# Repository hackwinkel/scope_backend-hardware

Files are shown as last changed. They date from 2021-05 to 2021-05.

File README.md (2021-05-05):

# 100Ms/s dual channel 16 bitdigital oscilloscope and function generator back-end with ethernet 

This repository contains the schematics and PCB design files.

# Main features
- 100MHz sample rate
- 2 channels, 16 bits A/D
- 4 channels, 14 bits D/A
- 256 Mbyte ddr3 ram
- Gigabit Ethernet

# General description
Please refer to the hierarchical schematic diagram provided in this repository

* Main (contains various digital power supplies and references to subsheets)
   * FPGA (contains the FPGA with its power connections, JTAG and signal definitions)
   * DACS (contains the D / A convertors with analogue power supplies and output buffers)
   * ADCS (contains the A/D convertors with analogue power supplies and input buffers)
   * ddr3 (contains memory with terminations)
   * GNET (contains Gbit ethernet PHY with magnetics and support components)

## Power supplies
All power supplies are standard LDO regulators, stepping down the voltages from a main 5V connection. To limit dissipation in each LDO, multiple 3.3V, 2.5V, 1.5V and 1.2V subnets are used, and the lower voltages are stepped down via an intermediary 3.3V stage.
The only exception is an optional switched mode power supply module providing +9V/-9V for analogue input/output buffers. This module is optional if the analogue front-end is used, as this also provides these voltages.

## FPGA
This project uses a SPARTAN 6 Field Programmable Logic Array (XC6SLX16 FPLA) at its heart. This FPLA device digitally connects all components, and allows this project to be flexibly reconfigured for various purposes. Core timing is provided by a 100MHz integrated crystal oscillator and a 125MHz clock derived from the ethernet PHY 

## DACS
Digital-to-Analogue conversion is performed by 4 DAC904 165 Msample/s 14 bit D/A convertors. Each of these D/A convertors has its own 3.3V power supply. The DAC904 produces a differential output signal, which is converted and buffered to a single ended signal using an OPA695 operational amplifier.

## ADCS
Analogue-to-Digital conversion is performed by 2 LTC2208 130 Msample/s 16 bit A/D convertors. Each of these A/D convertors has its own 3.3V power supply. For each A/D convertor an AD8138 diferential amplifier provides the required buffered differential analogue drive signal. These AD8138 are by default configured to convert a single ended signal to a differential signal.

## ddr3
A single MT41K128M16 ddr3 RAM chip provides 128M x 16 memory. This has to be a 1.5V compatible device as the SPARTAN 6 FPGA does not support 1.35V memory. Single ended, single direction lines (address and some control signals) are unterminated as this apparently "just works"-albeit probably not at maximum speed. Bidirectional signals are dynamically terminated on the chip. Simple resistive termination is provided on some differential clocking signals. A reference voltage is generated using a resistive divider. All traces on the PCB are length-matched to within 0.5mm

## GNET
A KSZ9031 Gigabit ethernet PHY with Reduced Gigabit Media Independent Interface (RGMII) provides a gigabit ethernet connection through a gigabit MagJack. The local 25Mhz crystal oscillator is converted to a 125MHz clock signal, which is also connected to the FPGA as an alternate timing source

## This project is currently under construction
Most notably, VHDL/Verilog code to program the FPGA is required and an analogue front-end.

# IMPORTANT NOTE FOR PCB FABRICATION

Various PCB houses have various design constraints. JLCPCB has some awkward design rules, requiring a larger space between via-pads and adjacent traces of different nets than between two traces of different nets. KiCAD only allows you to specify *one* spacing for both. In order to accomodate this, the PCB has been designed using 0.508mm vias with 0.2mm holes. Prior to exporting to gerbers, these via pads need to be made smaller in order to compy with these design rules:

Pcbnew -> Setup -> Design rules, change "Via Dia" to 0.45mm
Pcbnew -> Edit -> Edit All Tracks and Vias -> Set all vias (no tracks) to their Netclass value, and OK

## EXPORT GERBERS, DO NOT SAVE THE CHANGED PCB DESIGN FILES as next time you change anything the smaller vias will lead to planes and traces coming too close to the via.

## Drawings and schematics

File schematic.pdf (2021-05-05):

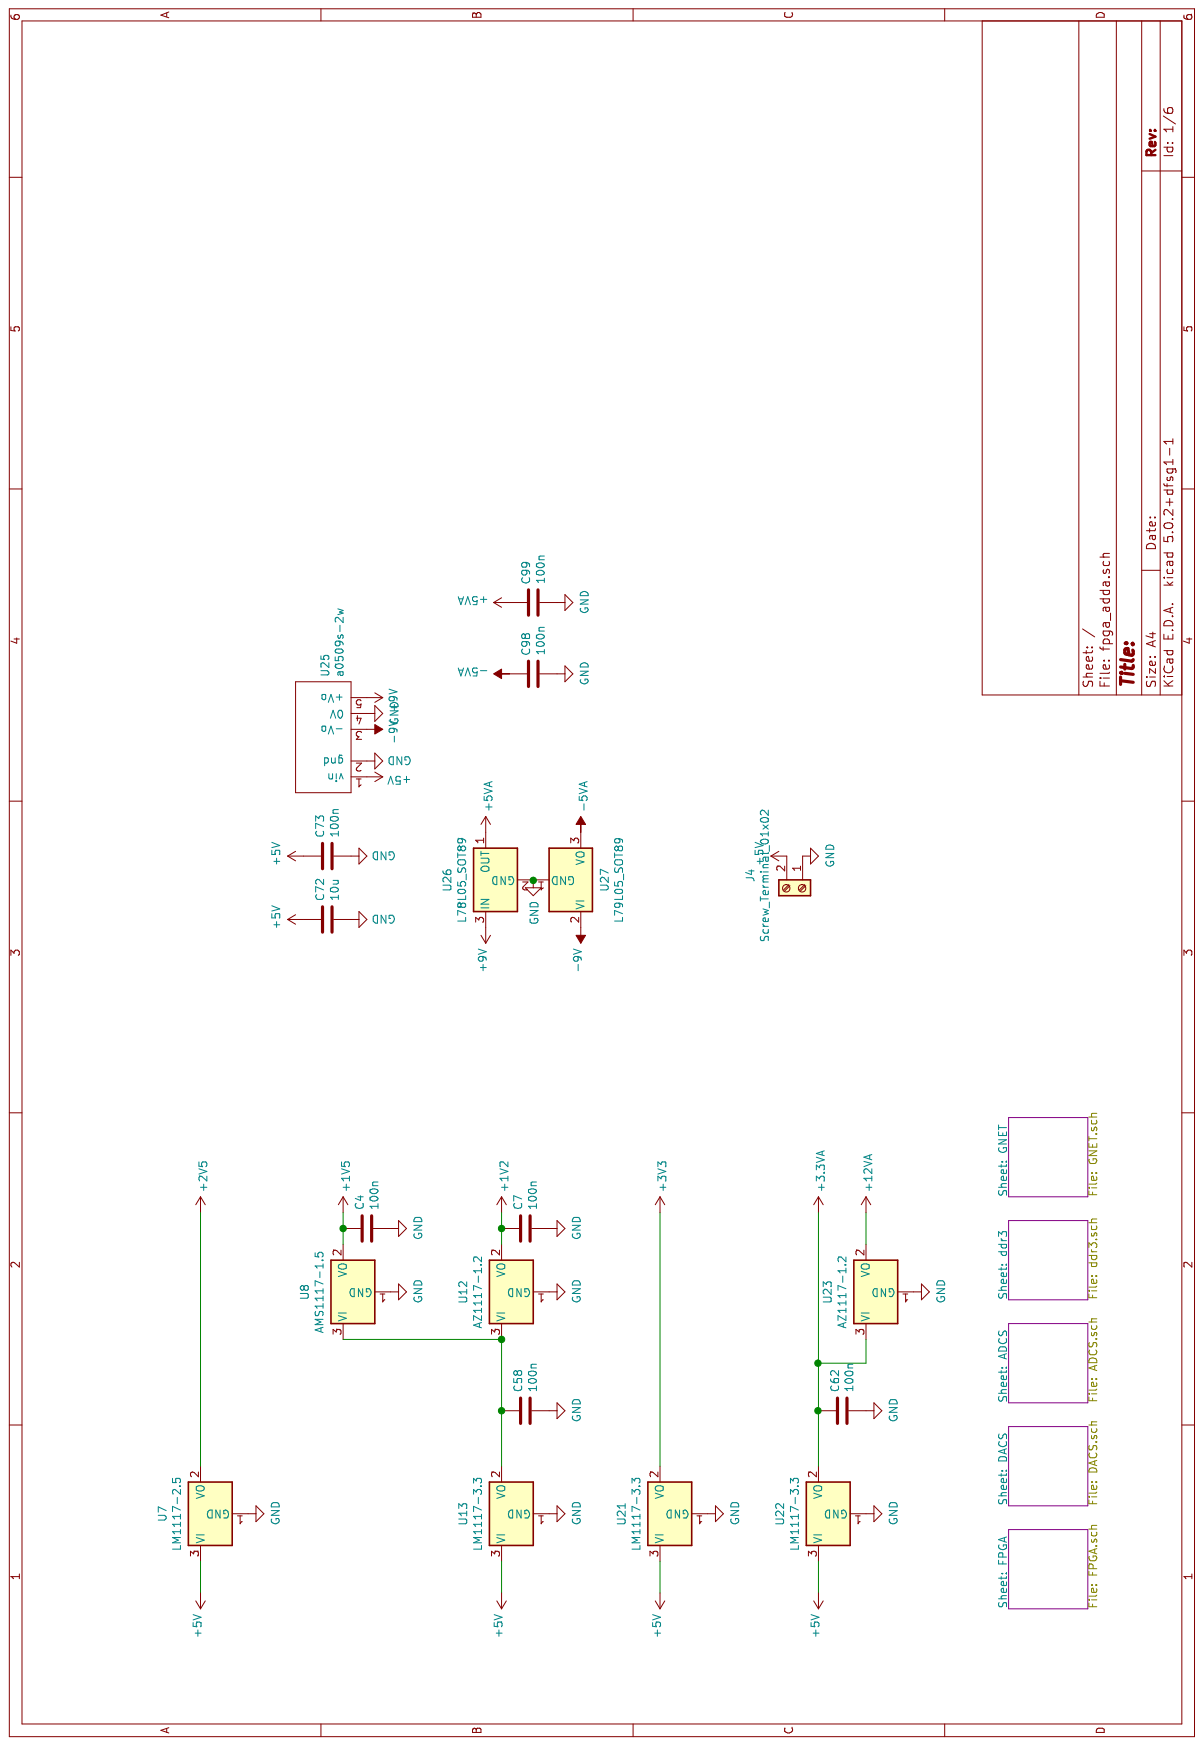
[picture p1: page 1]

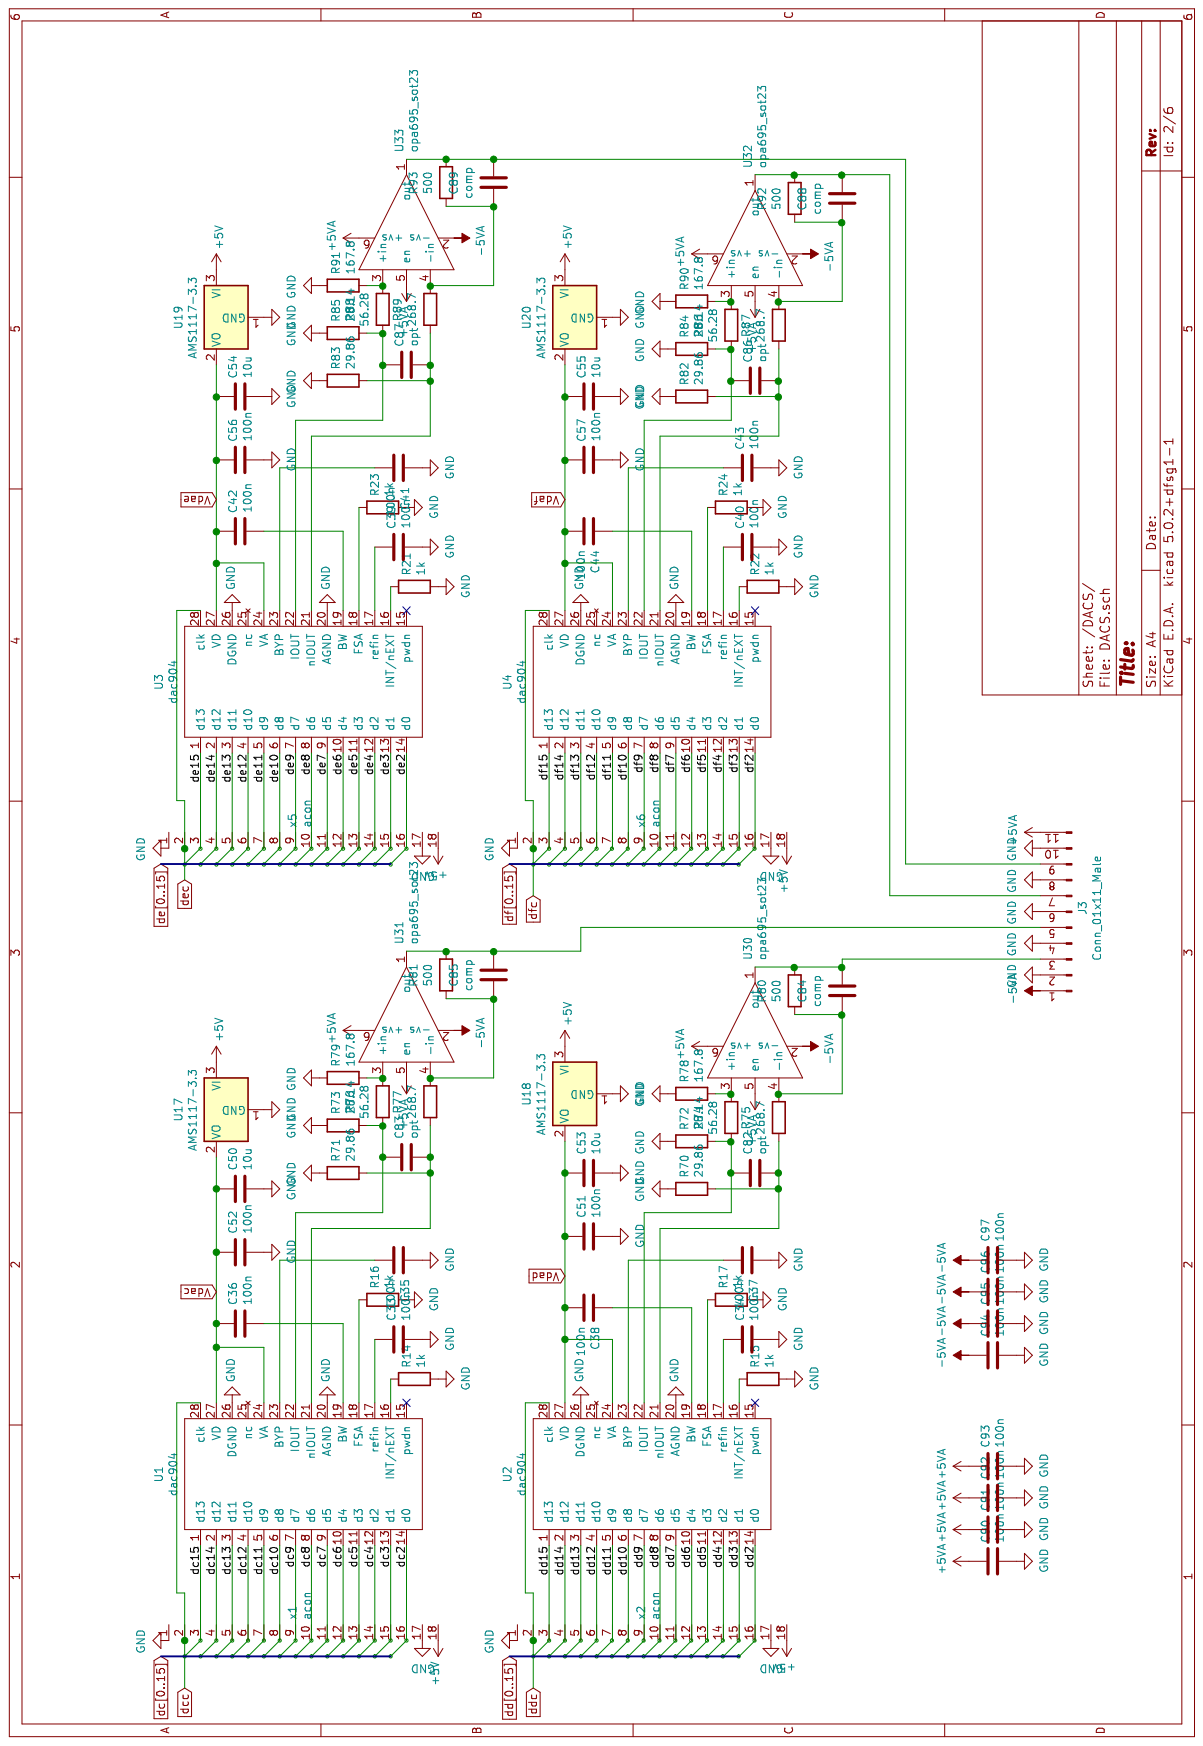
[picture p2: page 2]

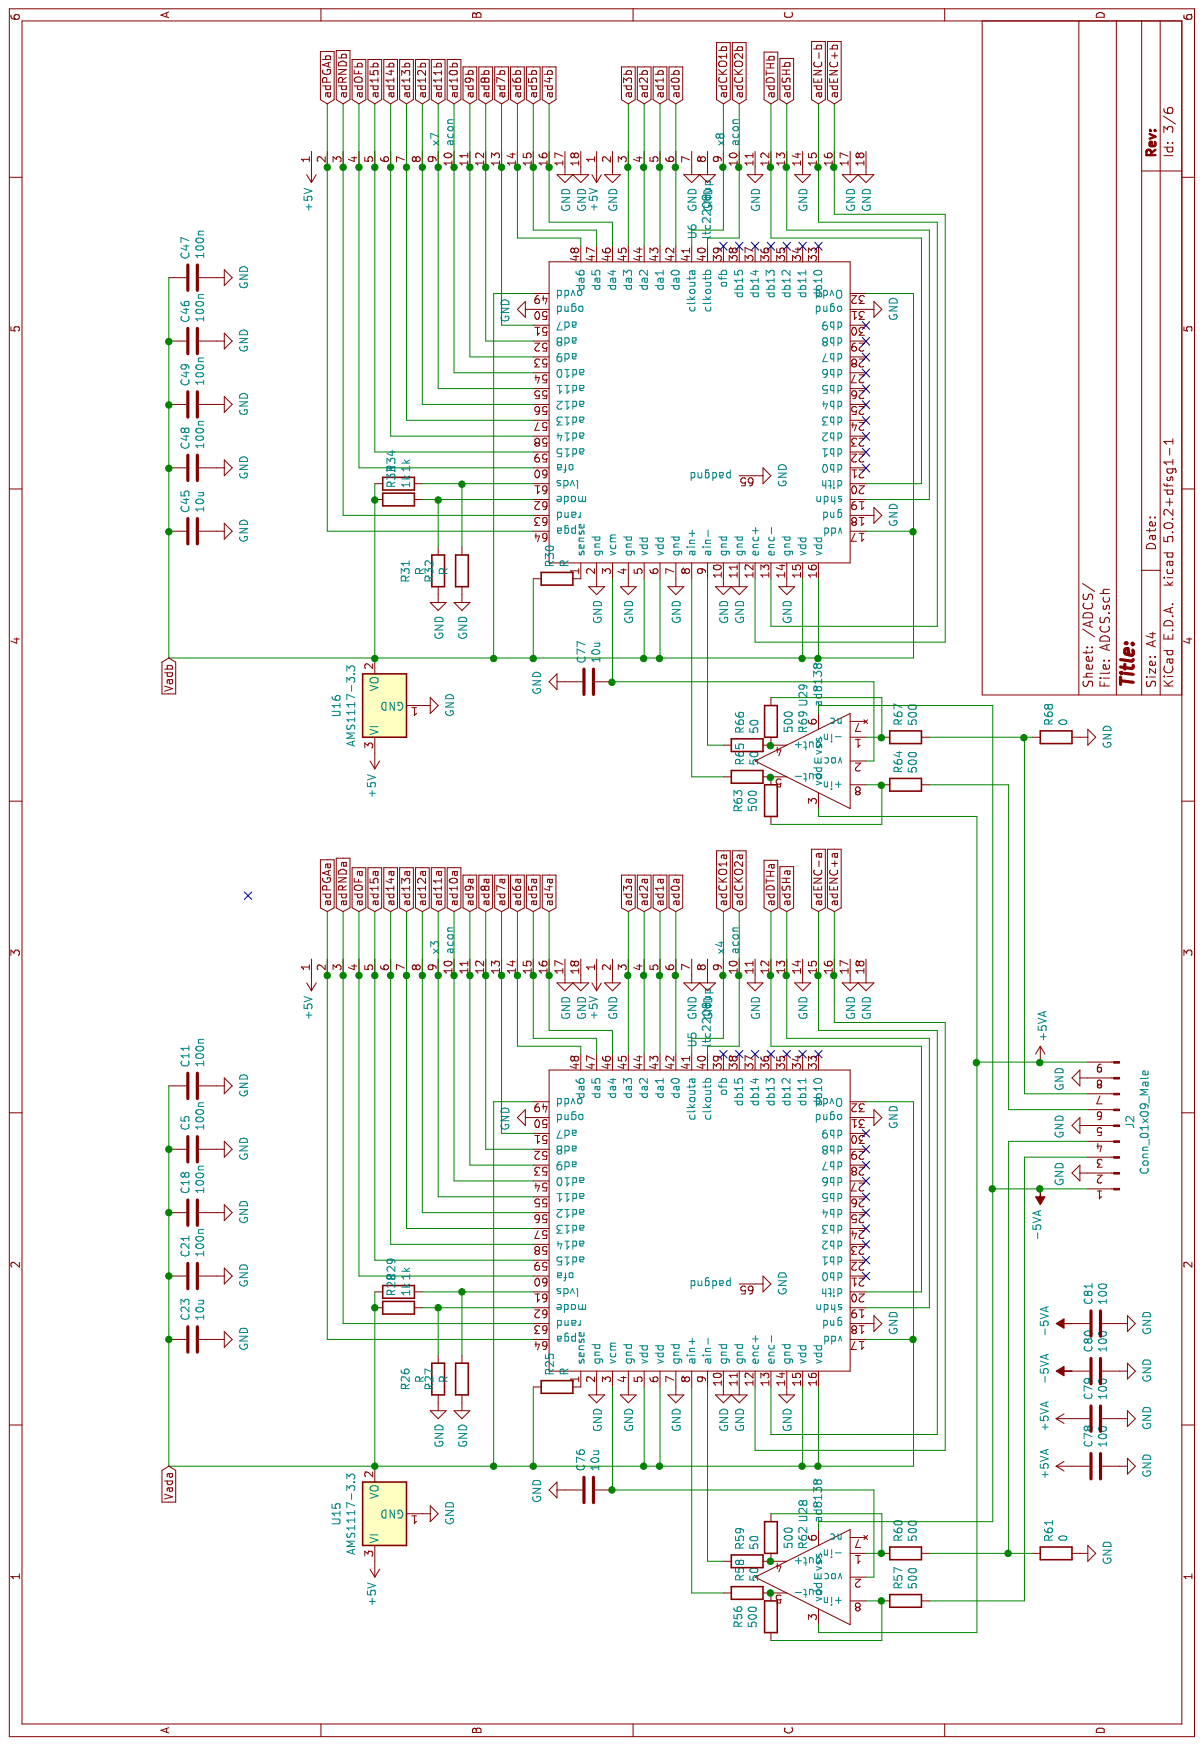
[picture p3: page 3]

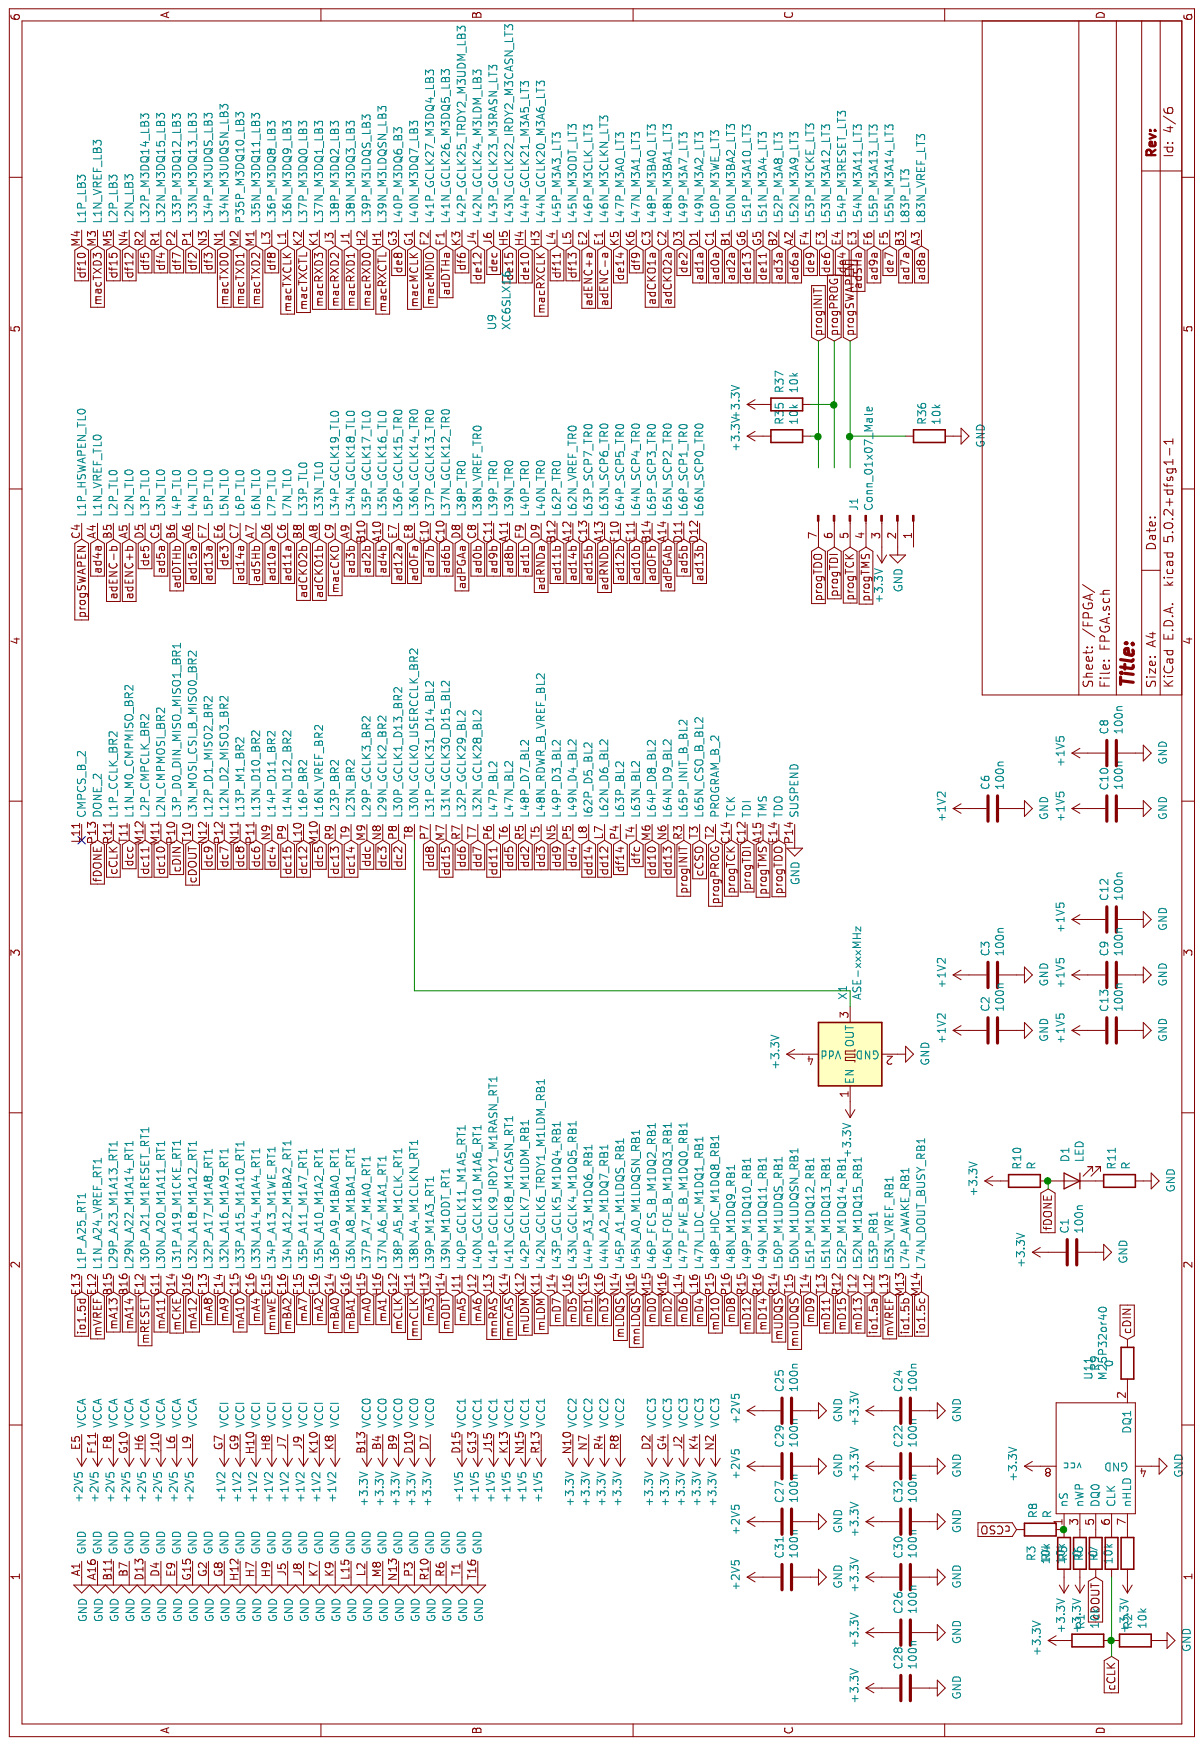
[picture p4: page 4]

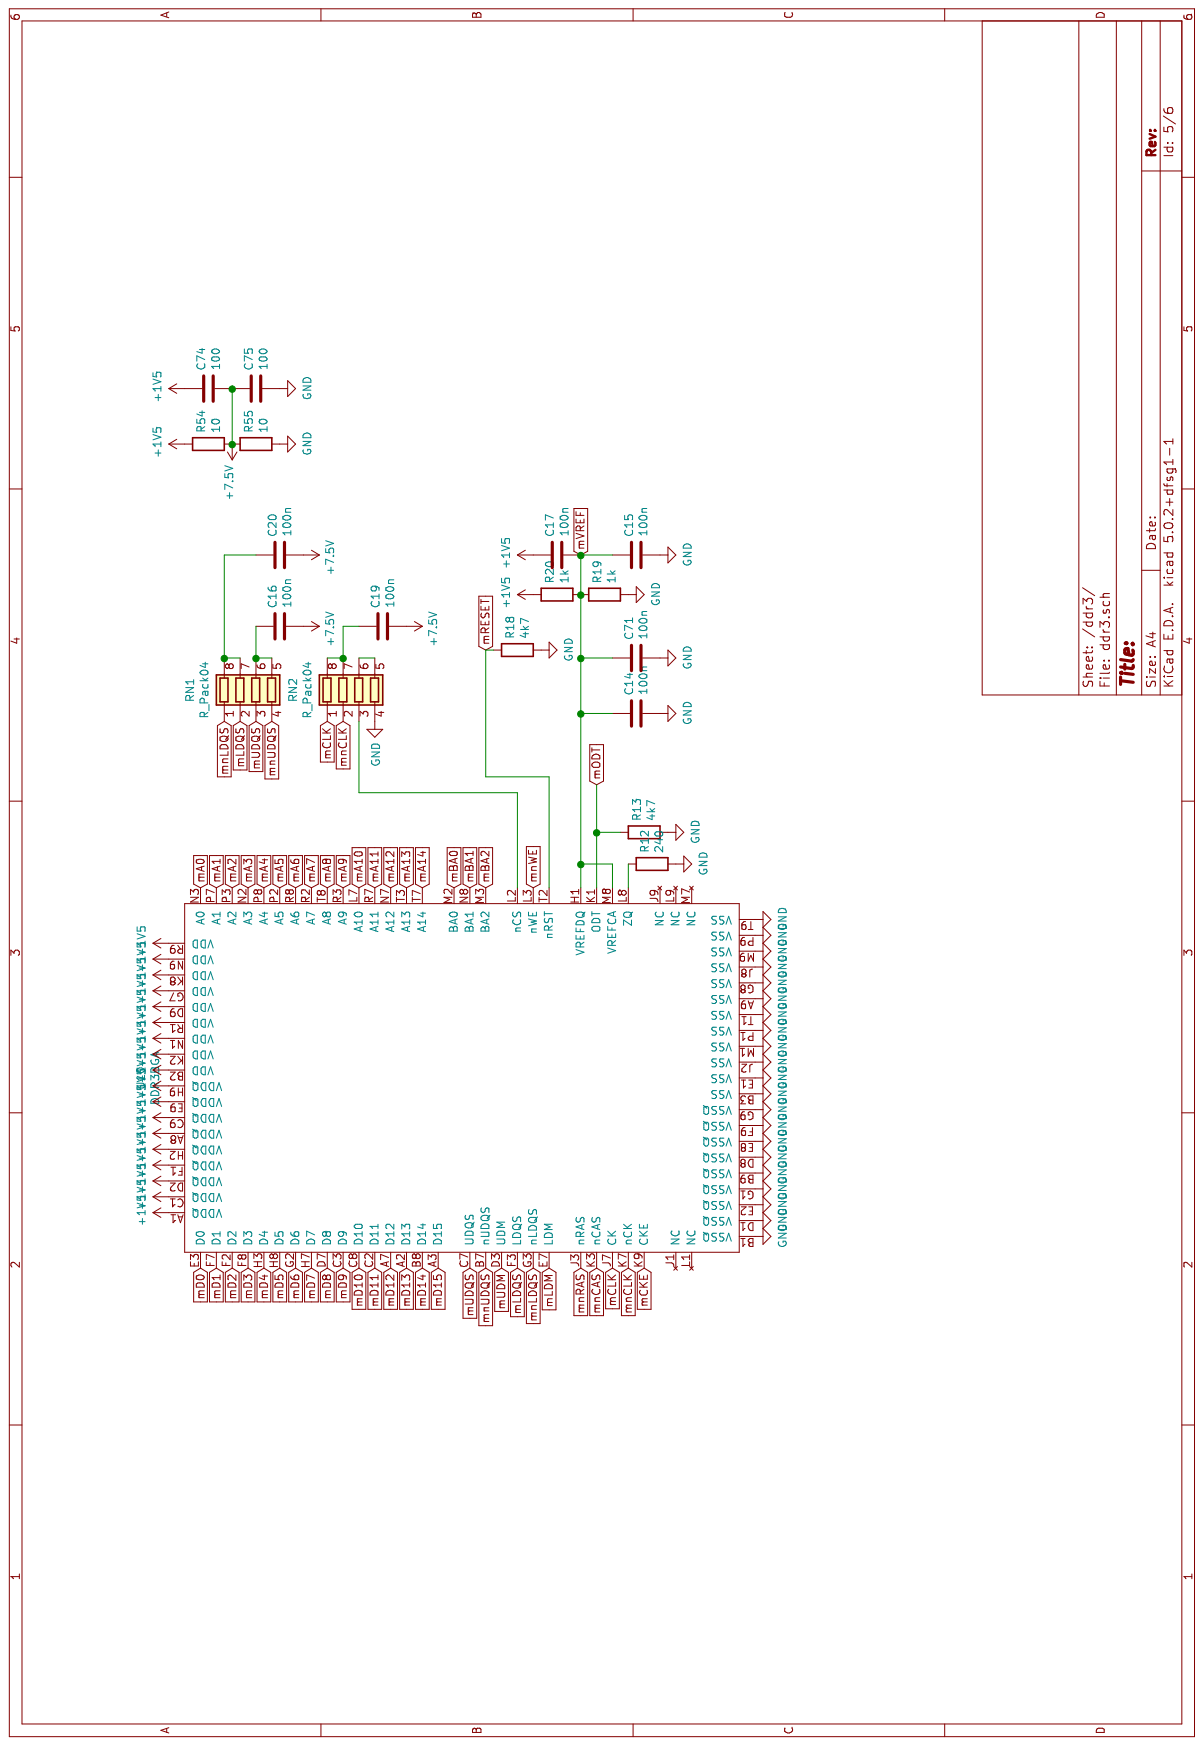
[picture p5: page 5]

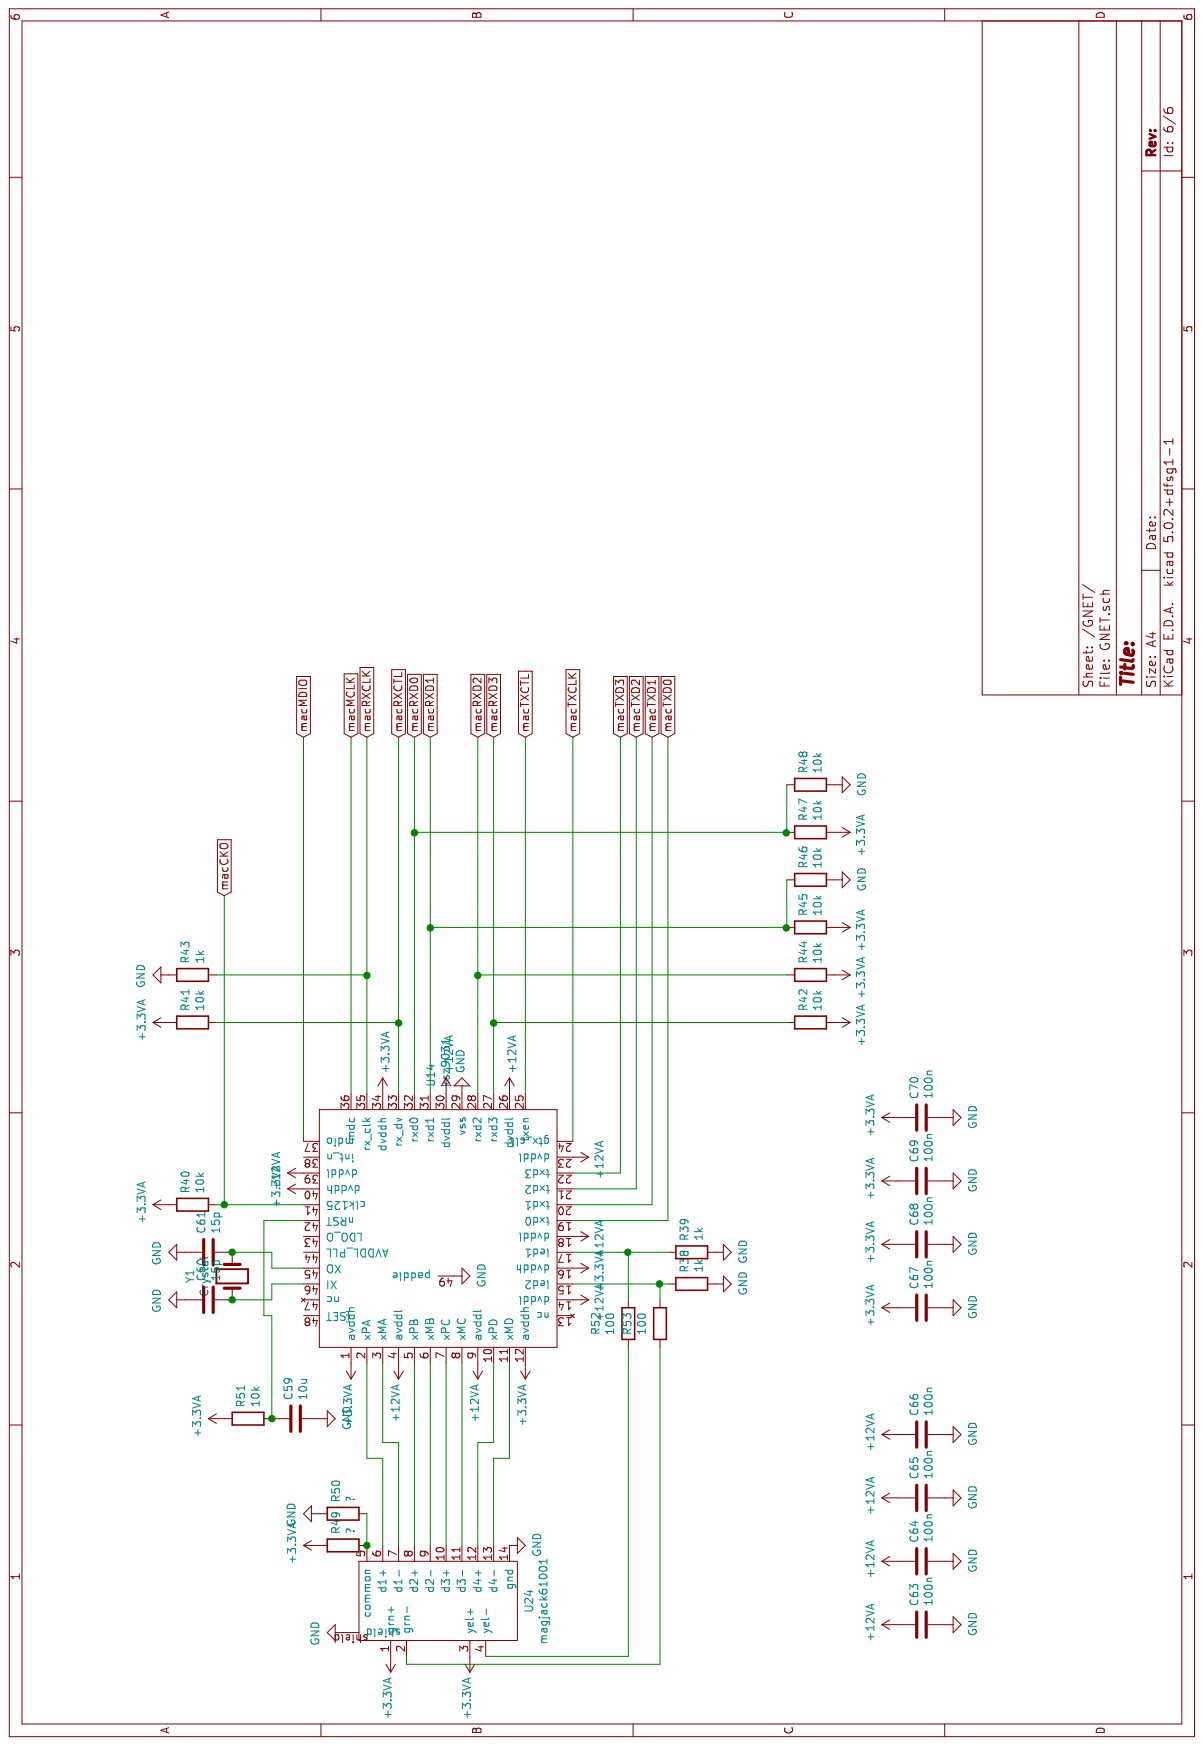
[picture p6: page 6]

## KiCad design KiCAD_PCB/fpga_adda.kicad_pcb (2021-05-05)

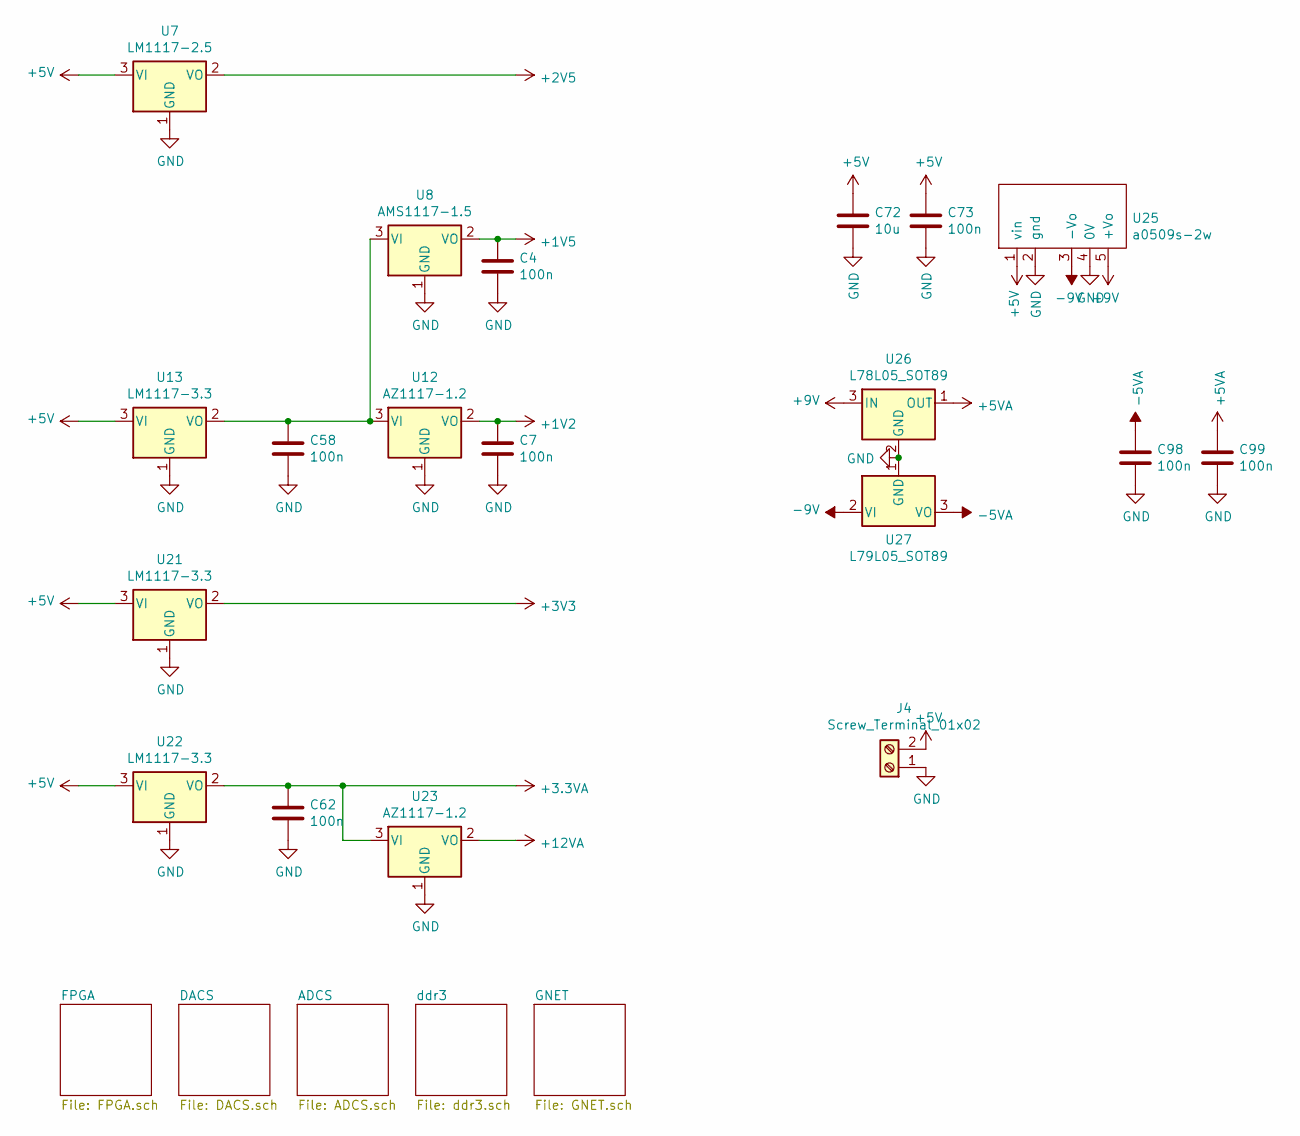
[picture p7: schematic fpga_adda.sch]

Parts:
C4, C7, C58, C62, C73, C98, C99: 100n; C_0805_2012Metric_Pad1.15x1.40mm_HandSolder
C72: 10u; C_0805_2012Metric_Pad1.15x1.40mm_HandSolder
J4: Screw_Terminal_01x02; TerminalBlock_bornier-2_P5.08mm
U7: LM1117-2.5; SOT-223-3_TabPin2
U8: AMS1117-1.5; SOT-223-3_TabPin2
U12, U23: AZ1117-1.2; SOT-223-3_TabPin2
U13, U21, U22: LM1117-3.3; SOT-223-3_TabPin2
U25: a0509s-2w
U26: L78L05_SOT89; SOT-89-3
U27: L79L05_SOT89; SOT-89-3

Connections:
+1V2: C7.1, U12.2 (VO); also elsewhere on the board
+1V5: C4.1, U8.2 (VO); also elsewhere on the board
+2V5: U7.2 (VO); also elsewhere on the board
+3.3VA: C62.1, U22.2 (VO), U23.3 (VI); also elsewhere on the board
+5V: C72.1, C73.1, J4.2, U7.3 (VI), U13.3 (VI), U21.3 (VI), U22.3 (VI), U25.1 (vin); also elsewhere on the board
+5VA: C99.1, U26.1 (OUT); also elsewhere on the board
+9V: U25.5 (+Vo), U26.3 (IN)
+12VA: U23.2 (VO); also elsewhere on the board
-5VA: C98.1, U27.3 (VO); also elsewhere on the board
-9V: U25.3 (-Vo), U27.2 (VI)
GND: C4.2, C7.2, C58.2, C62.2, C72.2, C73.2, C98.2, C99.2, J4.1, U7.1 (GND), U8.1 (GND), U12.1 (GND), U13.1 (GND), U21.1 (GND), U22.1 (GND), U23.1 (GND), U25.2 (gnd), U25.4 (0V), U26.2 (GND), U27.1 (GND); also elsewhere on the board
unnamed: C58.1, U8.3 (VI), U12.3 (VI), U13.2 (VO)

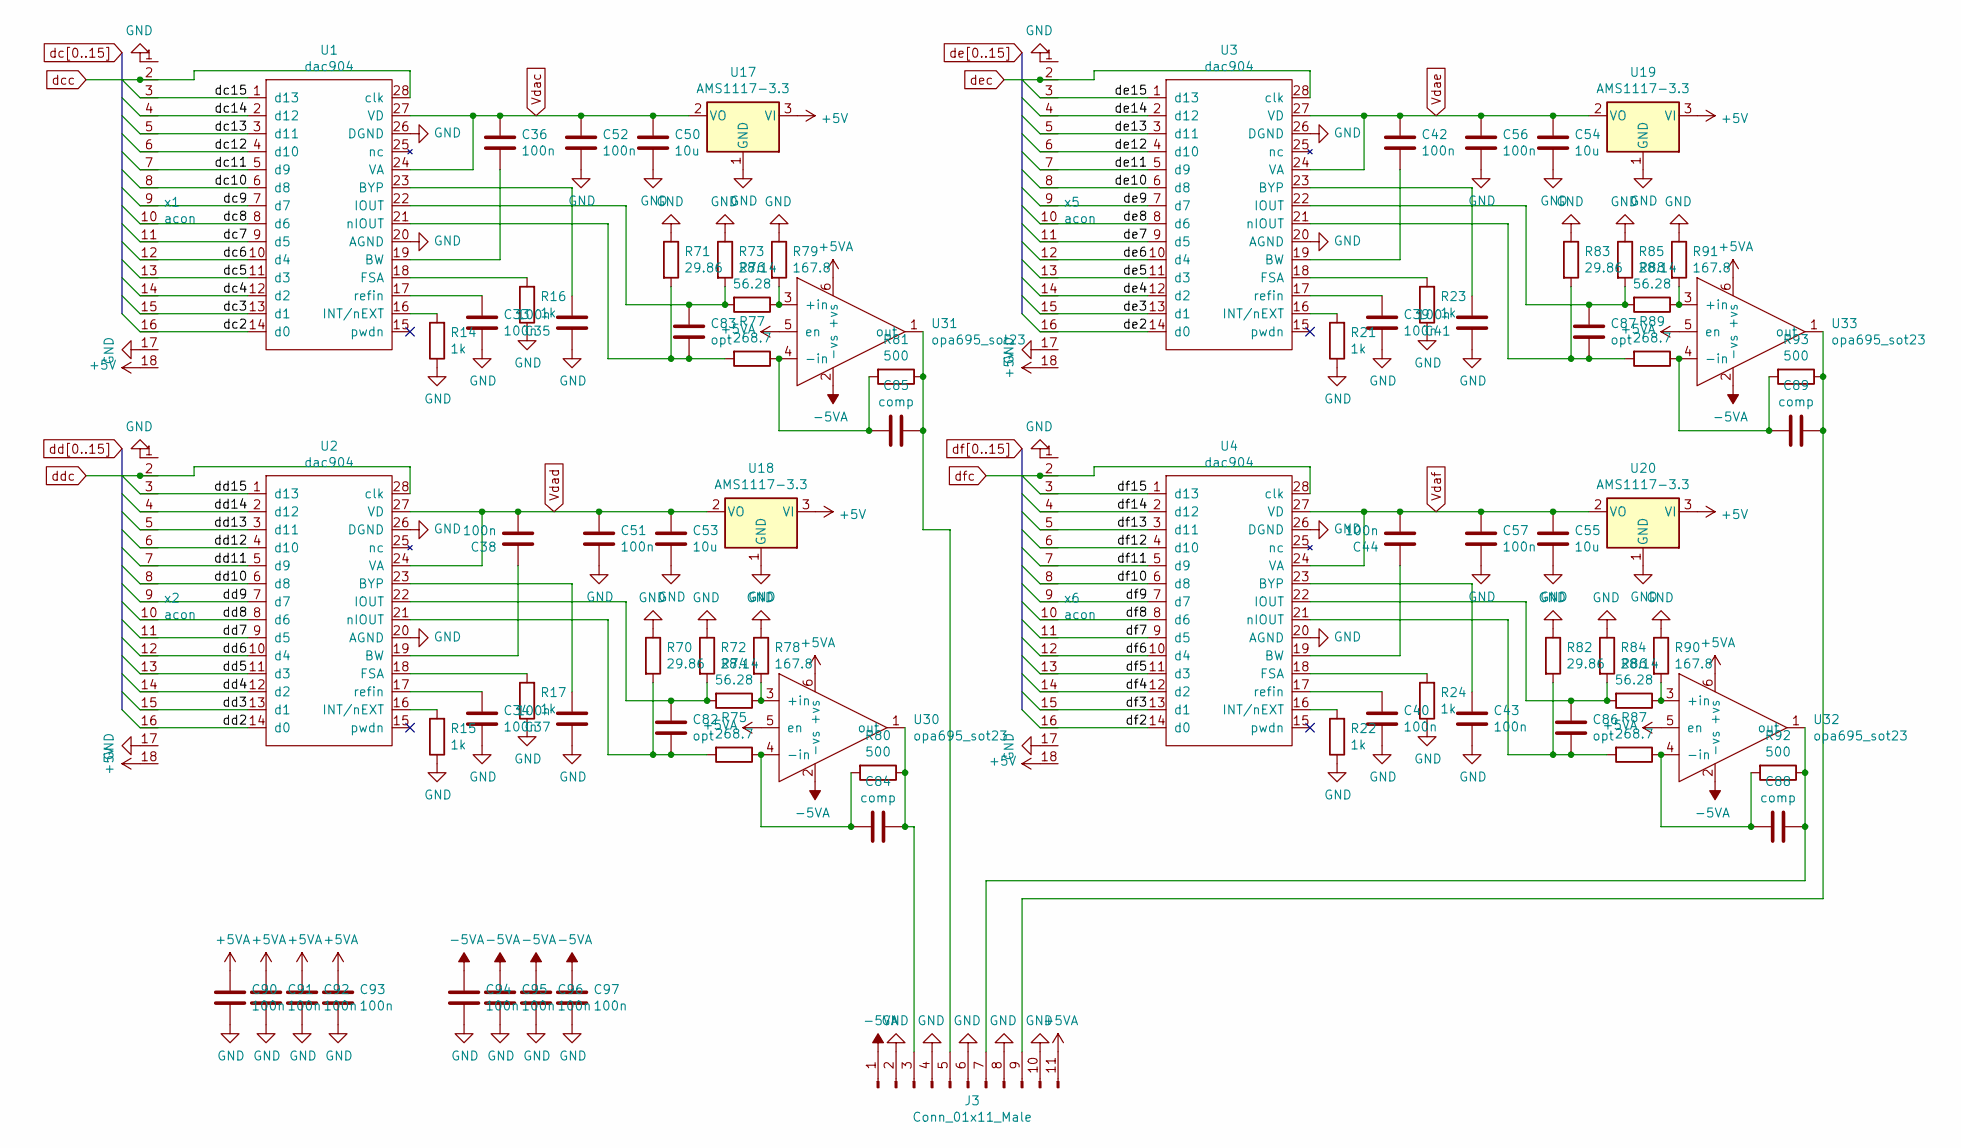
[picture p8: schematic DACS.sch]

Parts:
C33, C34, C35, C36, C37, C38, C39, C40, C41, C42, C43, C44, C51, C52, C56, C57, C90, C91, C92, C93, C94, C95, C96, C97: 100n; C_0805_2012Metric_Pad1.15x1.40mm_HandSolder
C50, C53, C54, C55: 10u; C_0805_2012Metric_Pad1.15x1.40mm_HandSolder
C82, C83, C86, C87: opt; C_0805_2012Metric_Pad1.15x1.40mm_HandSolder
C84, C85, C88, C89: comp; C_0805_2012Metric_Pad1.15x1.40mm_HandSolder
J3: Conn_01x11_Male; PinHeader_1x11_P2.54mm_Vertical
R14, R15, R16, R17, R21, R22, R23, R24: 1k; R_0805_2012Metric_Pad1.15x1.40mm_HandSolder
R70, R71, R82, R83: 29.86; R_0805_2012Metric_Pad1.15x1.40mm_HandSolder
R72, R73, R84, R85: 28.14; R_0805_2012Metric_Pad1.15x1.40mm_HandSolder
R74, R76, R86, R88: 56.28; R_0805_2012Metric_Pad1.15x1.40mm_HandSolder
R75, R77, R87, R89: 268.7; R_0805_2012Metric_Pad1.15x1.40mm_HandSolder
R78, R79, R90, R91: 167.8; R_0805_2012Metric_Pad1.15x1.40mm_HandSolder
R80, R81, R92, R93: 500; R_0805_2012Metric_Pad1.15x1.40mm_HandSolder
U1, U2, U3, U4: dac904; SSOP-28_5.3x10.2mm_P0.65mm
U17, U18, U19, U20: AMS1117-3.3; SOT-223-3_TabPin2
U30, U31, U32, U33: opa695_sot23; SOT-23-6_Handsoldering
x1, x2, x5, x6: acon

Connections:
+5V: U17.3 (VI), U18.3 (VI), U19.3 (VI), U20.3 (VI), x1.18, x2.18, x5.18, x6.18; also elsewhere on the board
+5VA: C90.1, C91.1, C92.1, C93.1, J3.11, U30.5 (en), U30.6 (+vs), U31.5 (en), U31.6 (+vs), U32.5 (en), U32.6 (+vs), U33.5 (en), U33.6 (+vs); also elsewhere on the board
-5VA: C94.1, C95.1, C96.1, C97.1, J3.1, U30.2 (-vs), U31.2 (-vs), U32.2 (-vs), U33.2 (-vs); also elsewhere on the board
GND: C33.2, C34.2, C35.1, C37.1, C39.2, C40.2, C41.1, C43.2, C50.2, C51.2, C52.2, C53.2, C54.2, C55.2, C56.2, C57.2, C90.2, C91.2, C92.2, C93.2, C94.2, C95.2, C96.2, C97.2, J3.2, J3.4, J3.6, J3.8, J3.10, R14.1, R15.1, R16.1, R17.1, R21.1, R22.1, R23.1, R24.1, R70.1, R71.1, R72.1, R73.1, R78.1, R79.1, R82.1, R83.1, R84.1, R85.1, R90.1, R91.1, U1.20 (AGND), U1.26 (DGND), U2.20 (AGND), U2.26 (DGND), U3.20 (AGND), U3.26 (DGND), U4.20 (AGND), U4.26 (DGND), U17.1 (GND), U18.1 (GND), U19.1 (GND), U20.1 (GND), x1.1, x1.17, x2.1, x2.17, x5.1, x5.17, x6.1, x6.17; also elsewhere on the board
unnamed: C33.1, U1.17 (refin)
unnamed: C34.1, U2.17 (refin)
unnamed: C35.2, U1.23 (BYP)
unnamed: C36.2, U1.19 (BW)
unnamed: C37.2, U2.23 (BYP)
unnamed: C38.1, U2.19 (BW)
unnamed: C39.1, U3.17 (refin)
unnamed: C40.1, U4.17 (refin)
unnamed: C41.2, U3.23 (BYP)
unnamed: C42.2, U3.19 (BW)
unnamed: C43.1, U4.23 (BYP)
unnamed: C44.1, U4.19 (BW)
unnamed: C82.1, R72.2, R74.2, U2.22 (IOUT)
unnamed: C82.2, R70.2, R75.2, U2.21 (nIOUT)
unnamed: C83.1, R73.2, R76.2, U1.22 (IOUT)
unnamed: C83.2, R71.2, R77.2, U1.21 (nIOUT)
unnamed: C84.1, J3.3, R80.1, U30.1 (out)
unnamed: C84.2, R75.1, R80.2, U30.4 (-in)
unnamed: C85.1, J3.5, R81.1, U31.1 (out)
unnamed: C85.2, R77.1, R81.2, U31.4 (-in)
unnamed: C86.1, R84.2, R86.2, U4.22 (IOUT)
unnamed: C86.2, R82.2, R87.2, U4.21 (nIOUT)
unnamed: C87.1, R85.2, R88.2, U3.22 (IOUT)
unnamed: C87.2, R83.2, R89.2, U3.21 (nIOUT)
unnamed: C88.1, J3.7, R92.1, U32.1 (out)
unnamed: C88.2, R87.1, R92.2, U32.4 (-in)
unnamed: C89.1, J3.9, R93.1, U33.1 (out)
unnamed: C89.2, R89.1, R93.2, U33.4 (-in)
unnamed: R14.2, U1.16 (INT/nEXT)
unnamed: R15.2, U2.16 (INT/nEXT)
unnamed: R16.2, U1.18 (FSA)
unnamed: R17.2, U2.18 (FSA)
unnamed: R21.2, U3.16 (INT/nEXT)
unnamed: R22.2, U4.16 (INT/nEXT)
unnamed: R23.2, U3.18 (FSA)
unnamed: R24.2, U4.18 (FSA)
unnamed: R74.1, R78.2, U30.3 (+in)
unnamed: R76.1, R79.2, U31.3 (+in)
unnamed: R86.1, R90.2, U32.3 (+in)
unnamed: R88.1, R91.2, U33.3 (+in)
Vdac: C36.1, C50.1, C52.1, U1.24 (VA), U1.27 (VD), U17.2 (VO)
Vdad: C38.2, C51.1, C53.1, U2.24 (VA), U2.27 (VD), U18.2 (VO)
Vdae: C42.1, C54.1, C56.1, U3.24 (VA), U3.27 (VD), U19.2 (VO)
Vdaf: C44.2, C55.1, C57.1, U4.24 (VA), U4.27 (VD), U20.2 (VO)
dc2: U1.14 (d0), x1.16; also elsewhere on the board
dc3: U1.13 (d1), x1.15; also elsewhere on the board
dc4: U1.12 (d2), x1.14; also elsewhere on the board
dc5: U1.11 (d3), x1.13; also elsewhere on the board
dc6: U1.10 (d4), x1.12; also elsewhere on the board
dc7: U1.9 (d5), x1.11; also elsewhere on the board
dc8: U1.8 (d6), x1.10; also elsewhere on the board
dc9: U1.7 (d7), x1.9; also elsewhere on the board
dc10: U1.6 (d8), x1.8; also elsewhere on the board
dc11: U1.5 (d9), x1.7; also elsewhere on the board
dc12: U1.4 (d10), x1.6; also elsewhere on the board
dc13: U1.3 (d11), x1.5; also elsewhere on the board
dc14: U1.2 (d12), x1.4; also elsewhere on the board
dc15: U1.1 (d13), x1.3; also elsewhere on the board
dcc: U1.28 (clk), x1.2; also elsewhere on the board
dd2: U2.14 (d0), x2.16; also elsewhere on the board
dd3: U2.13 (d1), x2.15; also elsewhere on the board
dd4: U2.12 (d2), x2.14; also elsewhere on the board
dd5: U2.11 (d3), x2.13; also elsewhere on the board
dd6: U2.10 (d4), x2.12; also elsewhere on the board
dd7: U2.9 (d5), x2.11; also elsewhere on the board
dd8: U2.8 (d6), x2.10; also elsewhere on the board
dd9: U2.7 (d7), x2.9; also elsewhere on the board
dd10: U2.6 (d8), x2.8; also elsewhere on the board
dd11: U2.5 (d9), x2.7; also elsewhere on the board
dd12: U2.4 (d10), x2.6; also elsewhere on the board
dd13: U2.3 (d11), x2.5; also elsewhere on the board
dd14: U2.2 (d12), x2.4; also elsewhere on the board
dd15: U2.1 (d13), x2.3; also elsewhere on the board
ddc: U2.28 (clk), x2.2; also elsewhere on the board
de2: U3.14 (d0), x5.16; also elsewhere on the board
de3: U3.13 (d1), x5.15; also elsewhere on the board
de4: U3.12 (d2), x5.14; also elsewhere on the board
de5: U3.11 (d3), x5.13; also elsewhere on the board
de6: U3.10 (d4), x5.12; also elsewhere on the board
de7: U3.9 (d5), x5.11; also elsewhere on the board
de8: U3.8 (d6), x5.10; also elsewhere on the board
de9: U3.7 (d7), x5.9; also elsewhere on the board
de10: U3.6 (d8), x5.8; also elsewhere on the board
de11: U3.5 (d9), x5.7; also elsewhere on the board
de12: U3.4 (d10), x5.6; also elsewhere on the board
de13: U3.3 (d11), x5.5; also elsewhere on the board
de14: U3.2 (d12), x5.4; also elsewhere on the board
de15: U3.1 (d13), x5.3; also elsewhere on the board
dec: U3.28 (clk), x5.2; also elsewhere on the board
df2: U4.14 (d0), x6.16; also elsewhere on the board
df3: U4.13 (d1), x6.15; also elsewhere on the board
df4: U4.12 (d2), x6.14; also elsewhere on the board
df5: U4.11 (d3), x6.13; also elsewhere on the board
df6: U4.10 (d4), x6.12; also elsewhere on the board
df7: U4.9 (d5), x6.11; also elsewhere on the board
df8: U4.8 (d6), x6.10; also elsewhere on the board
df9: U4.7 (d7), x6.9; also elsewhere on the board
df10: U4.6 (d8), x6.8; also elsewhere on the board
df11: U4.5 (d9), x6.7; also elsewhere on the board
df12: U4.4 (d10), x6.6; also elsewhere on the board
df13: U4.3 (d11), x6.5; also elsewhere on the board
df14: U4.2 (d12), x6.4; also elsewhere on the board
df15: U4.1 (d13), x6.3; also elsewhere on the board
dfc: U4.28 (clk), x6.2; also elsewhere on the board

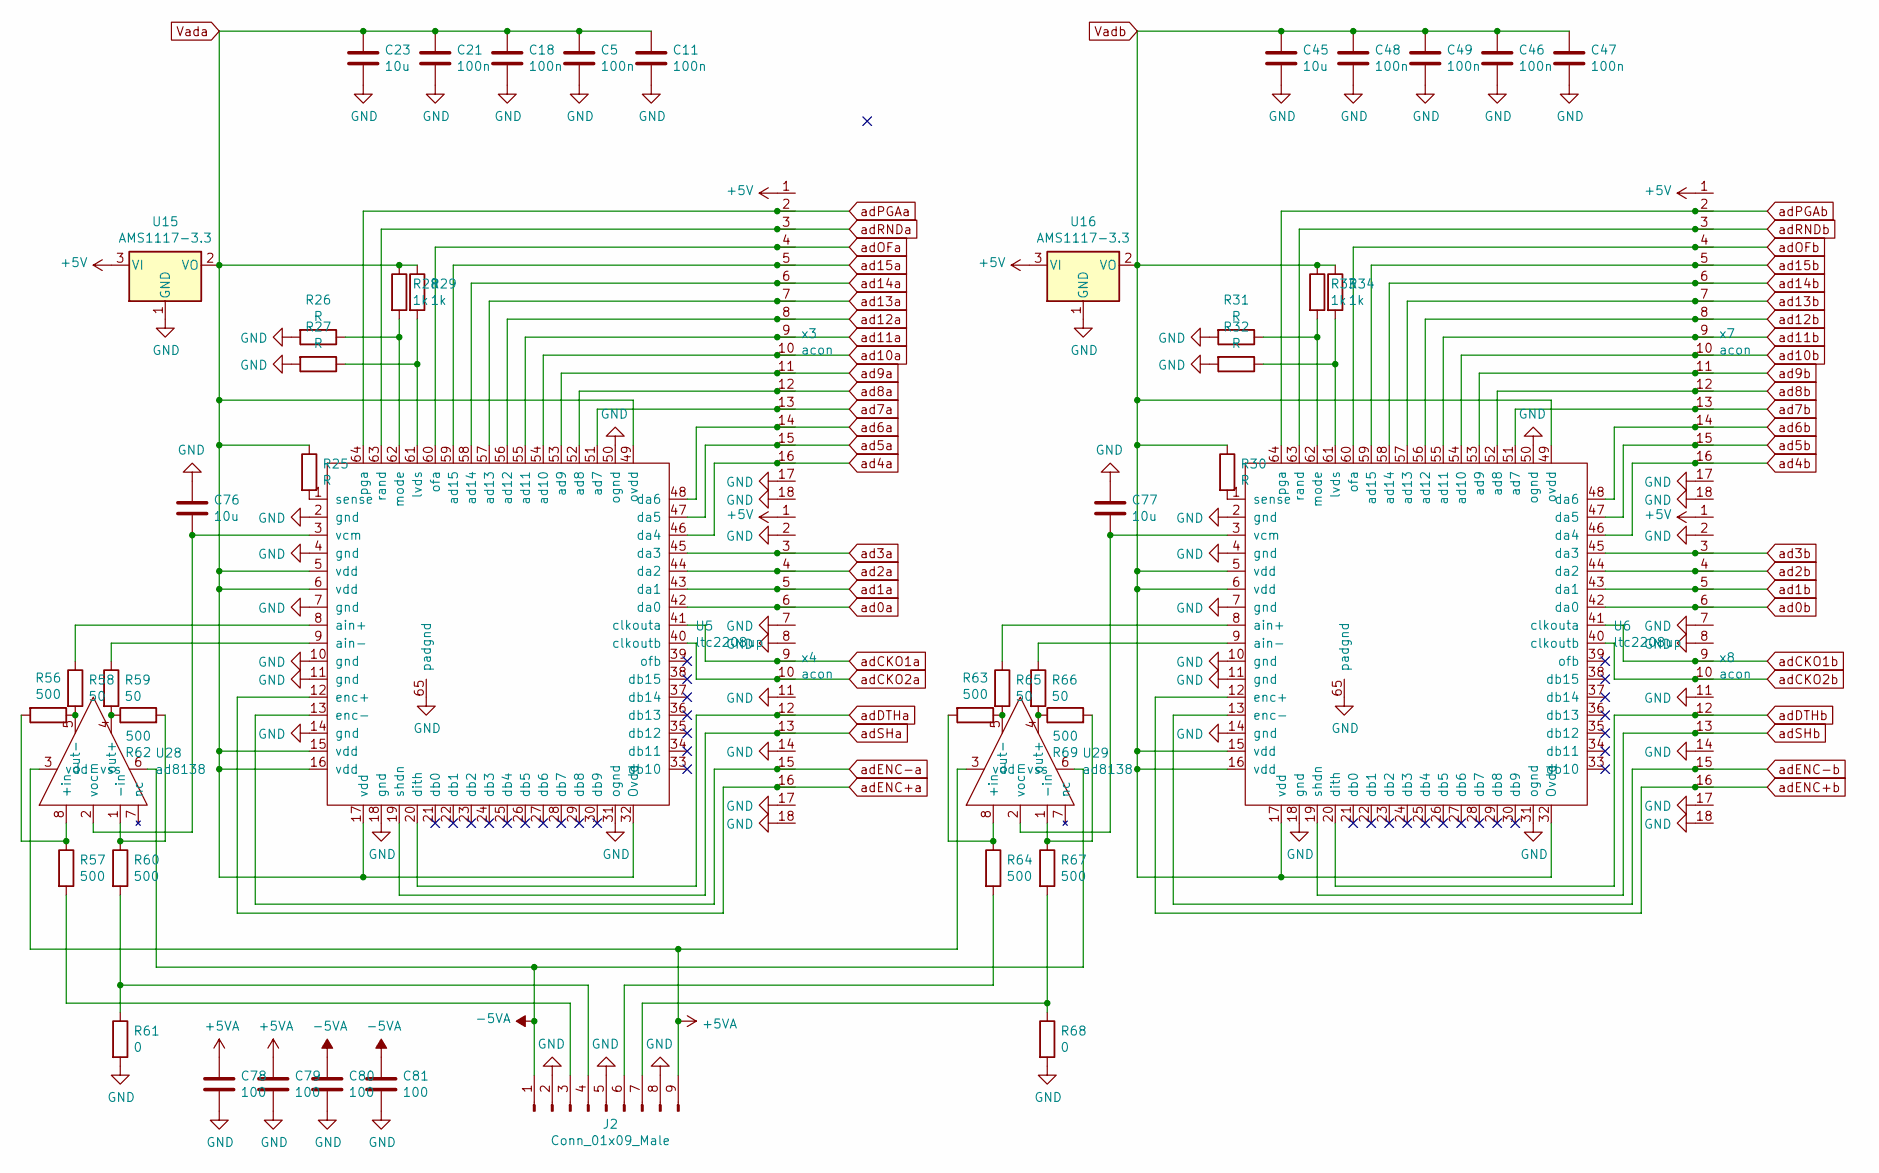
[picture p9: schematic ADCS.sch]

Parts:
C5, C11, C18, C21, C46, C47, C48, C49: 100n; C_0805_2012Metric_Pad1.15x1.40mm_HandSolder
C23, C45, C76, C77: 10u; C_0805_2012Metric_Pad1.15x1.40mm_HandSolder
C78, C79, C80, C81: 100; C_0805_2012Metric_Pad1.15x1.40mm_HandSolder
J2: Conn_01x09_Male; PinHeader_1x09_P2.54mm_Vertical
R25, R26, R27, R30, R31, R32: R; R_0805_2012Metric_Pad1.15x1.40mm_HandSolder
R28, R29, R33, R34: 1k; R_0805_2012Metric_Pad1.15x1.40mm_HandSolder
R56, R57, R60, R62, R63, R64, R67, R69: 500; R_0805_2012Metric_Pad1.15x1.40mm_HandSolder
R58, R59, R65, R66: 50; R_0805_2012Metric_Pad1.15x1.40mm_HandSolder
R61, R68: 0; R_0805_2012Metric_Pad1.15x1.40mm_HandSolder
U5, U6: ltc2208up; ltc2208
U15, U16: AMS1117-3.3; SOT-223-3_TabPin2
U28, U29: ad8138; SO-8_5.3x6.2mm_P1.27mm
x3, x4, x7, x8: acon

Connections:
+5V: U15.3 (VI), U16.3 (VI), x3.1, x4.1, x7.1, x8.1; also elsewhere on the board
+5VA: C78.1, C79.1, J2.9, U28.3 (vdd), U29.3 (vdd); also elsewhere on the board
-5VA: C80.1, C81.1, J2.1, U28.6 (vss), U29.6 (vss); also elsewhere on the board
GND: C5.2, C11.2, C18.2, C21.2, C23.2, C45.2, C46.2, C47.2, C48.2, C49.2, C76.2, C77.1, C78.2, C79.2, C80.2, C81.2, J2.2, J2.5, J2.8, R26.2, R27.2, R31.2, R32.2, R61.2, R68.2, U5.2 (gnd), U5.4 (gnd), U5.7 (gnd), U5.10 (gnd), U5.11 (gnd), U5.14 (gnd), U5.18 (gnd), U5.31 (ognd), U5.50 (ognd), U5.65 (padgnd), U6.2 (gnd), U6.4 (gnd), U6.7 (gnd), U6.10 (gnd), U6.11 (gnd), U6.14 (gnd), U6.18 (gnd), U6.31 (ognd), U6.50 (ognd), U6.65 (padgnd), U15.1 (GND), U16.1 (GND), x3.17, x3.18, x4.2, x4.7, x4.8, x4.11, x4.14, x4.17, x4.18, x7.17, x7.18, x8.2, x8.7, x8.8, x8.11, x8.14, x8.17, x8.18; also elsewhere on the board
unnamed: C76.1, U5.3 (vcm), U28.2 (vocm)
unnamed: C77.2, U6.3 (vcm), U29.2 (vocm)
unnamed: J2.3, R57.2
unnamed: J2.4, R60.2, R61.1
unnamed: J2.6, R64.2
unnamed: J2.7, R67.2, R68.1
unnamed: R25.2, U5.1 (sense)
unnamed: R26.1, R28.2, U5.62 (mode)
unnamed: R27.1, R29.2, U5.61 (lvds)
unnamed: R30.2, U6.1 (sense)
unnamed: R31.1, R33.2, U6.62 (mode)
unnamed: R32.1, R34.2, U6.61 (lvds)
unnamed: R56.1, R58.2, U28.5 (out-)
unnamed: R56.2, R57.1, U28.8 (+in)
unnamed: R58.1, U5.8 (ain+)
unnamed: R59.1, U5.9 (ain-)
unnamed: R59.2, R62.1, U28.4 (out+)
unnamed: R60.1, R62.2, U28.1 (-in)
unnamed: R63.1, R65.2, U29.5 (out-)
unnamed: R63.2, R64.1, U29.8 (+in)
unnamed: R65.1, U6.8 (ain+)
unnamed: R66.1, U6.9 (ain-)
unnamed: R66.2, R69.1, U29.4 (out+)
unnamed: R67.1, R69.2, U29.1 (-in)
Vada: C5.1, C11.1, C18.1, C21.1, C23.1, R25.1, R28.1, R29.1, U5.5 (vdd), U5.6 (vdd), U5.15 (vdd), U5.16 (vdd), U5.17 (vdd), U5.32 (Ovdd), U5.49 (ovdd), U15.2 (VO)
Vadb: C45.1, C46.1, C47.1, C48.1, C49.1, R30.1, R33.1, R34.1, U6.5 (vdd), U6.6 (vdd), U6.15 (vdd), U6.16 (vdd), U6.17 (vdd), U6.32 (Ovdd), U6.49 (ovdd), U16.2 (VO)
ad0a: U5.42 (da0), x4.6; also elsewhere on the board
ad0b: U6.42 (da0), x8.6; also elsewhere on the board
ad1a: U5.43 (da1), x4.5; also elsewhere on the board
ad1b: U6.43 (da1), x8.5; also elsewhere on the board
ad2a: U5.44 (da2), x4.4; also elsewhere on the board
ad2b: U6.44 (da2), x8.4; also elsewhere on the board
ad3a: U5.45 (da3), x4.3; also elsewhere on the board
ad3b: U6.45 (da3), x8.3; also elsewhere on the board
ad4a: U5.46 (da4), x3.16; also elsewhere on the board
ad4b: U6.46 (da4), x7.16; also elsewhere on the board
ad5a: U5.47 (da5), x3.15; also elsewhere on the board
ad5b: U6.47 (da5), x7.15; also elsewhere on the board
ad6a: U5.48 (da6), x3.14; also elsewhere on the board
ad6b: U6.48 (da6), x7.14; also elsewhere on the board
ad7a: U5.51 (ad7), x3.13; also elsewhere on the board
ad7b: U6.51 (ad7), x7.13; also elsewhere on the board
ad8a: U5.52 (ad8), x3.12; also elsewhere on the board
ad8b: U6.52 (ad8), x7.12; also elsewhere on the board
ad9a: U5.53 (ad9), x3.11; also elsewhere on the board
ad9b: U6.53 (ad9), x7.11; also elsewhere on the board
ad10a: U5.54 (ad10), x3.10; also elsewhere on the board
ad10b: U6.54 (ad10), x7.10; also elsewhere on the board
ad11a: U5.55 (ad11), x3.9; also elsewhere on the board
ad11b: U6.55 (ad11), x7.9; also elsewhere on the board
ad12a: U5.56 (ad12), x3.8; also elsewhere on the board
ad12b: U6.56 (ad12), x7.8; also elsewhere on the board
ad13a: U5.57 (ad13), x3.7; also elsewhere on the board
ad13b: U6.57 (ad13), x7.7; also elsewhere on the board
ad14a: U5.58 (ad14), x3.6; also elsewhere on the board
ad14b: U6.58 (ad14), x7.6; also elsewhere on the board
ad15a: U5.59 (ad15), x3.5; also elsewhere on the board
ad15b: U6.59 (ad15), x7.5; also elsewhere on the board
adCKO1a: U5.41 (clkouta), x4.9; also elsewhere on the board
adCKO1b: U6.41 (clkouta), x8.9; also elsewhere on the board
adCKO2a: U5.40 (clkoutb), x4.10; also elsewhere on the board
adCKO2b: U6.40 (clkoutb), x8.10; also elsewhere on the board
adDTHa: U5.20 (dith), x4.12; also elsewhere on the board
adDTHb: U6.20 (dith), x8.12; also elsewhere on the board
adENC+a: U5.12 (enc+), x4.16; also elsewhere on the board
adENC+b: U6.12 (enc+), x8.16; also elsewhere on the board
adENC-a: U5.13 (enc-), x4.15; also elsewhere on the board
adENC-b: U6.13 (enc-), x8.15; also elsewhere on the board
adOFa: U5.60 (ofa), x3.4; also elsewhere on the board
adOFb: U6.60 (ofa), x7.4; also elsewhere on the board
adPGAa: U5.64 (pga), x3.2; also elsewhere on the board
adPGAb: U6.64 (pga), x7.2; also elsewhere on the board
adRNDa: U5.63 (rand), x3.3; also elsewhere on the board
adRNDb: U6.63 (rand), x7.3; also elsewhere on the board
adSHa: U5.19 (shdn), x4.13; also elsewhere on the board
adSHb: U6.19 (shdn), x8.13; also elsewhere on the board

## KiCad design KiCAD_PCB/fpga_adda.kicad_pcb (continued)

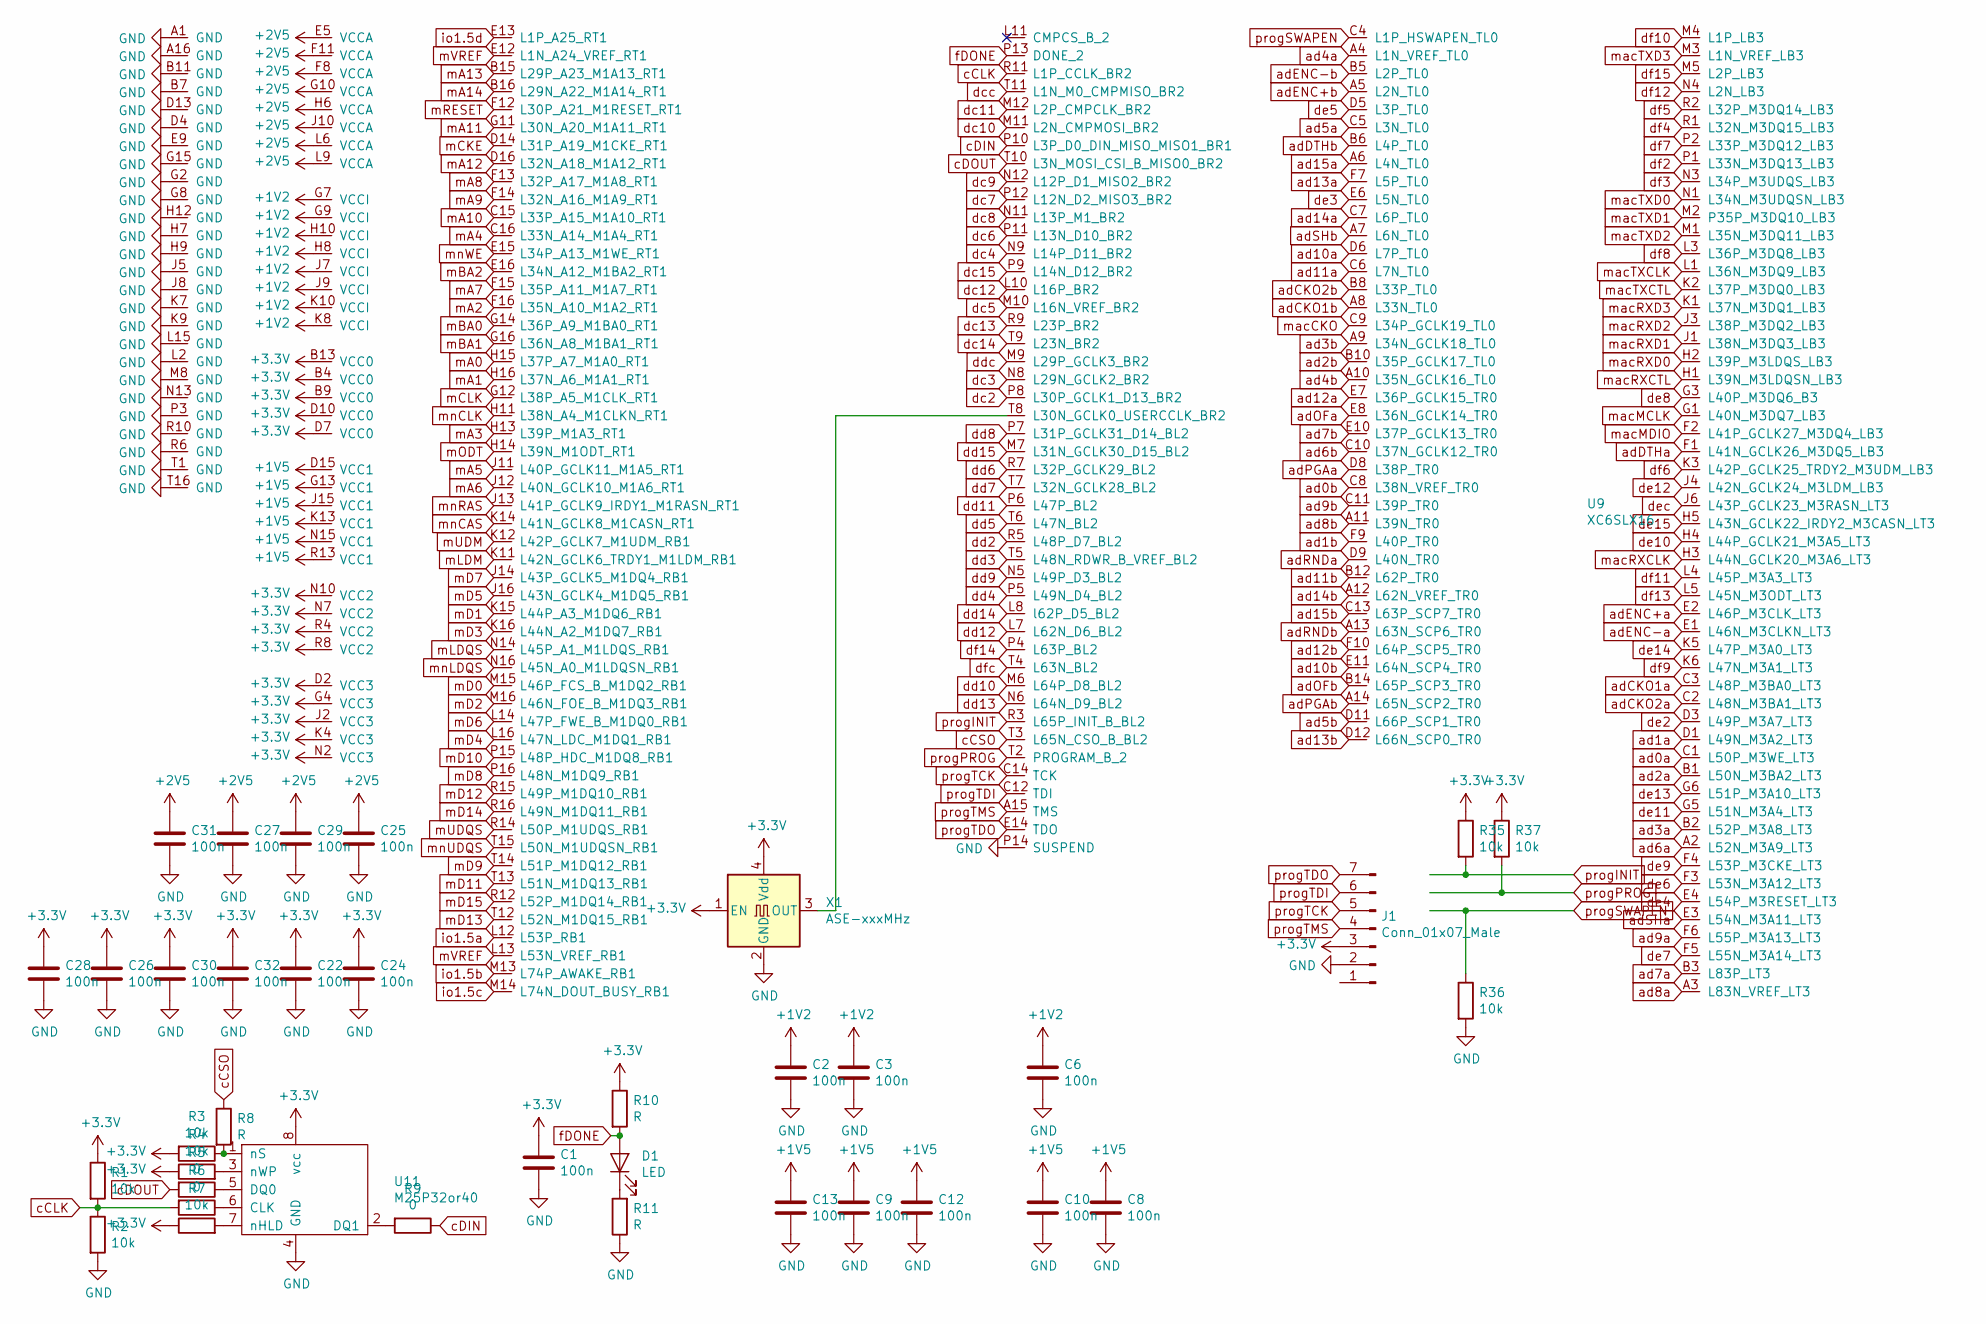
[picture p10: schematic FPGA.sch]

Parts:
C1, C2, C3, C6, C8, C9, C10, C12, C13, C22, C24, C25, C26, C27, C28, C29, C30, C31, C32: 100n; C_0805_2012Metric_Pad1.15x1.40mm_HandSolder
D1: LED; LED_0805_2012Metric_Pad1.15x1.40mm_HandSolder
J1: Conn_01x07_Male; jtagconn
R1, R2, R3, R4, R7, R35, R36, R37: 10k; R_0805_2012Metric_Pad1.15x1.40mm_HandSolder
R5, R6, R9: 0; R_0805_2012Metric_Pad1.15x1.40mm_HandSolder
R8, R10, R11: R; R_0805_2012Metric_Pad1.15x1.40mm_HandSolder
U9: XC6SLX16; xc6_FTG256
U11: M25P32or40
X1: ASE-xxxMHz; Oscillator_SMD_Abracon_ASV-4Pin_7.0x5.1mm_HandSoldering

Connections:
+1V2: C2.1, C3.1, C6.1, U9.G7 (VCCI), U9.G9 (VCCI), U9.H8 (VCCI), U9.H10 (VCCI), U9.J7 (VCCI), U9.J9 (VCCI), U9.K8 (VCCI), U9.K10 (VCCI); also elsewhere on the board
+1V5: C8.1, C9.1, C10.1, C12.1, C13.1, U9.D15 (VCC1), U9.G13 (VCC1), U9.J15 (VCC1), U9.K13 (VCC1), U9.N15 (VCC1), U9.R13 (VCC1); also elsewhere on the board
+2V5: C25.1, C27.1, C29.1, C31.1, U9.E5 (VCCA), U9.F8 (VCCA), U9.F11 (VCCA), U9.G10 (VCCA), U9.H6 (VCCA), U9.J10 (VCCA), U9.L6 (VCCA), U9.L9 (VCCA); also elsewhere on the board
GND: C1.2, C2.2, C3.2, C6.2, C8.2, C9.2, C10.2, C12.2, C13.2, C22.2, C24.2, C25.2, C26.2, C27.2, C28.2, C29.2, C30.2, C31.2, C32.2, J1.2, R2.2, R11.1, R36.2, U9.A1 (GND), U9.A16 (GND), U9.B7 (GND), U9.B11 (GND), U9.D4 (GND), U9.D13 (GND), U9.E9 (GND), U9.G2 (GND), U9.G8 (GND), U9.G15 (GND), U9.H7 (GND), U9.H9 (GND), U9.H12 (GND), U9.J5 (GND), U9.J8 (GND), U9.K7 (GND), U9.K9 (GND), U9.L2 (GND), U9.L15 (GND), U9.M8 (GND), U9.N13 (GND), U9.P3 (GND), U9.P14 (SUSPEND), U9.R6 (GND), U9.R10 (GND), U9.T1 (GND), U9.T16 (GND), U11.4 (GND), X1.2 (GND); also elsewhere on the board
unnamed: D1.1 (K), R11.2
unnamed: R3.1, R8.2, U11.1 (nS)
unnamed: R4.2, U11.3 (nWP)
unnamed: R5.1, U11.5 (DQ0)
unnamed: R6.1, U11.6 (CLK)
unnamed: R7.2, U11.7 (nHLD)
unnamed: R9.2, U11.2 (DQ1)
unnamed: U9.T8 (L30N_GCLK0_USERCCLK_BR2), X1.3 (OUT)
ad0a: U9.C1 (L50P_M3WE_LT3); also elsewhere on the board
ad0b: U9.C8 (L38N_VREF_TR0); also elsewhere on the board
ad1a: U9.D1 (L49N_M3A2_LT3); also elsewhere on the board
ad1b: U9.F9 (L40P_TR0); also elsewhere on the board
ad2a: U9.B1 (L50N_M3BA2_LT3); also elsewhere on the board
ad2b: U9.B10 (L35P_GCLK17_TL0); also elsewhere on the board
ad3a: U9.B2 (L52P_M3A8_LT3); also elsewhere on the board
ad3b: U9.A9 (L34N_GCLK18_TL0); also elsewhere on the board
ad4a: U9.A4 (L1N_VREF_TL0); also elsewhere on the board
ad4b: U9.A10 (L35N_GCLK16_TL0); also elsewhere on the board
ad5a: U9.C5 (L3N_TL0); also elsewhere on the board
ad5b: U9.D11 (L66P_SCP1_TR0); also elsewhere on the board
ad6a: U9.A2 (L52N_M3A9_LT3); also elsewhere on the board
ad6b: U9.C10 (L37N_GCLK12_TR0); also elsewhere on the board
ad7a: U9.B3 (L83P_LT3); also elsewhere on the board
ad7b: U9.E10 (L37P_GCLK13_TR0); also elsewhere on the board
ad8a: U9.A3 (L83N_VREF_LT3); also elsewhere on the board
ad8b: U9.A11 (L39N_TR0); also elsewhere on the board
ad9a: U9.F6 (L55P_M3A13_LT3); also elsewhere on the board
ad9b: U9.C11 (L39P_TR0); also elsewhere on the board
ad10a: U9.D6 (L7P_TL0); also elsewhere on the board
ad10b: U9.E11 (L64N_SCP4_TR0); also elsewhere on the board
ad11a: U9.C6 (L7N_TL0); also elsewhere on the board
ad11b: U9.B12 (L62P_TR0); also elsewhere on the board
ad12a: U9.E7 (L36P_GCLK15_TR0); also elsewhere on the board
ad12b: U9.F10 (L64P_SCP5_TR0); also elsewhere on the board
ad13a: U9.F7 (L5P_TL0); also elsewhere on the board
ad13b: U9.D12 (L66N_SCP0_TR0); also elsewhere on the board
ad14a: U9.C7 (L6P_TL0); also elsewhere on the board
ad14b: U9.A12 (L62N_VREF_TR0); also elsewhere on the board
ad15a: U9.A6 (L4N_TL0); also elsewhere on the board
ad15b: U9.C13 (L63P_SCP7_TR0); also elsewhere on the board
adCKO1a: U9.C3 (L48P_M3BA0_LT3); also elsewhere on the board
adCKO1b: U9.A8 (L33N_TL0); also elsewhere on the board
adCKO2a: U9.C2 (L48N_M3BA1_LT3); also elsewhere on the board
adCKO2b: U9.B8 (L33P_TL0); also elsewhere on the board
adDTHa: U9.F1 (L41N_GCLK26_M3DQ5_LB3); also elsewhere on the board
adDTHb: U9.B6 (L4P_TL0); also elsewhere on the board
adENC+a: U9.E2 (L46P_M3CLK_LT3); also elsewhere on the board
adENC+b: U9.A5 (L2N_TL0); also elsewhere on the board
adENC-a: U9.E1 (L46N_M3CLKN_LT3); also elsewhere on the board
adENC-b: U9.B5 (L2P_TL0); also elsewhere on the board
adOFa: U9.E8 (L36N_GCLK14_TR0); also elsewhere on the board
adOFb: U9.B14 (L65P_SCP3_TR0); also elsewhere on the board
adPGAa: U9.D8 (L38P_TR0); also elsewhere on the board
adPGAb: U9.A14 (L65N_SCP2_TR0); also elsewhere on the board
adRNDa: U9.D9 (L40N_TR0); also elsewhere on the board
adRNDb: U9.A13 (L63N_SCP6_TR0); also elsewhere on the board
adSHa: U9.E3 (L54N_M3A11_LT3); also elsewhere on the board
adSHb: U9.A7 (L6N_TL0); also elsewhere on the board
cCLK: R1.2, R2.1, R6.2, U9.R11 (L1P_CCLK_BR2)
cCSO: R8.1, U9.T3 (L65N_CSO_B_BL2)
cDIN: R9.1, U9.P10 (L3P_D0_DIN_MISO_MISO1_BR1)
cDOUT: R5.2, U9.T10 (L3N_MOSI_CSI_B_MISO0_BR2)
dc2: U9.P8 (L30P_GCLK1_D13_BR2); also elsewhere on the board
dc3: U9.N8 (L29N_GCLK2_BR2); also elsewhere on the board
dc4: U9.N9 (L14P_D11_BR2); also elsewhere on the board
dc5: U9.M10 (L16N_VREF_BR2); also elsewhere on the board
dc6: U9.P11 (L13N_D10_BR2); also elsewhere on the board
dc7: U9.P12 (L12N_D2_MISO3_BR2); also elsewhere on the board
dc8: U9.N11 (L13P_M1_BR2); also elsewhere on the board
dc9: U9.N12 (L12P_D1_MISO2_BR2); also elsewhere on the board
dc10: U9.M11 (L2N_CMPMOSI_BR2); also elsewhere on the board
dc11: U9.M12 (L2P_CMPCLK_BR2); also elsewhere on the board
dc12: U9.L10 (L16P_BR2); also elsewhere on the board
dc13: U9.R9 (L23P_BR2); also elsewhere on the board
dc14: U9.T9 (L23N_BR2); also elsewhere on the board
dc15: U9.P9 (L14N_D12_BR2); also elsewhere on the board
dcc: U9.T11 (L1N_M0_CMPMISO_BR2); also elsewhere on the board
dd2: U9.R5 (L48P_D7_BL2); also elsewhere on the board
dd3: U9.T5 (L48N_RDWR_B_VREF_BL2); also elsewhere on the board
dd4: U9.P5 (L49N_D4_BL2); also elsewhere on the board
dd5: U9.T6 (L47N_BL2); also elsewhere on the board
dd6: U9.R7 (L32P_GCLK29_BL2); also elsewhere on the board
dd7: U9.T7 (L32N_GCLK28_BL2); also elsewhere on the board
dd8: U9.P7 (L31P_GCLK31_D14_BL2); also elsewhere on the board
dd9: U9.N5 (L49P_D3_BL2); also elsewhere on the board
dd10: U9.M6 (L64P_D8_BL2); also elsewhere on the board
dd11: U9.P6 (L47P_BL2); also elsewhere on the board
dd12: U9.L7 (L62N_D6_BL2); also elsewhere on the board
dd13: U9.N6 (L64N_D9_BL2); also elsewhere on the board
dd14: U9.L8 (l62P_D5_BL2); also elsewhere on the board
dd15: U9.M7 (L31N_GCLK30_D15_BL2); also elsewhere on the board
ddc: U9.M9 (L29P_GCLK3_BR2); also elsewhere on the board
de2: U9.D3 (L49P_M3A7_LT3); also elsewhere on the board
de3: U9.E6 (L5N_TL0); also elsewhere on the board
de4: U9.E4 (L54P_M3RESET_LT3); also elsewhere on the board
de5: U9.D5 (L3P_TL0); also elsewhere on the board
de6: U9.F3 (L53N_M3A12_LT3); also elsewhere on the board
de7: U9.F5 (L55N_M3A14_LT3); also elsewhere on the board
de8: U9.G3 (L40P_M3DQ6_B3); also elsewhere on the board
de9: U9.F4 (L53P_M3CKE_LT3); also elsewhere on the board
de10: U9.H4 (L44P_GCLK21_M3A5_LT3); also elsewhere on the board
de11: U9.G5 (L51N_M3A4_LT3); also elsewhere on the board
de12: U9.J4 (L42N_GCLK24_M3LDM_LB3); also elsewhere on the board
de13: U9.G6 (L51P_M3A10_LT3); also elsewhere on the board
de14: U9.K5 (L47P_M3A0_LT3); also elsewhere on the board
de15: U9.H5 (L43N_GCLK22_IRDY2_M3CASN_LT3); also elsewhere on the board
dec: U9.J6 (L43P_GCLK23_M3RASN_LT3); also elsewhere on the board
df2: U9.P1 (L33N_M3DQ13_LB3); also elsewhere on the board
df3: U9.N3 (L34P_M3UDQS_LB3); also elsewhere on the board
df4: U9.R1 (L32N_M3DQ15_LB3); also elsewhere on the board
df5: U9.R2 (L32P_M3DQ14_LB3); also elsewhere on the board
df6: U9.K3 (L42P_GCLK25_TRDY2_M3UDM_LB3); also elsewhere on the board
df7: U9.P2 (L33P_M3DQ12_LB3); also elsewhere on the board
df8: U9.L3 (L36P_M3DQ8_LB3); also elsewhere on the board
df9: U9.K6 (L47N_M3A1_LT3); also elsewhere on the board
df10: U9.M4 (L1P_LB3); also elsewhere on the board
df11: U9.L4 (L45P_M3A3_LT3); also elsewhere on the board
df12: U9.N4 (L2N_LB3); also elsewhere on the board
df13: U9.L5 (L45N_M3ODT_LT3); also elsewhere on the board
df14: U9.P4 (L63P_BL2); also elsewhere on the board
df15: U9.M5 (L2P_LB3); also elsewhere on the board
dfc: U9.T4 (L63N_BL2); also elsewhere on the board
fDONE: D1.2 (A), R10.2, U9.P13 (DONE_2)
io1.5a: U9.L12 (L53P_RB1)
io1.5b: U9.M13 (L74P_AWAKE_RB1)
io1.5c: U9.M14 (L74N_DOUT_BUSY_RB1)
io1.5d: U9.E13 (L1P_A25_RT1)
mA0: U9.H15 (L37P_A7_M1A0_RT1); also elsewhere on the board
mA1: U9.H16 (L37N_A6_M1A1_RT1); also elsewhere on the board
mA2: U9.F16 (L35N_A10_M1A2_RT1); also elsewhere on the board
mA3: U9.H13 (L39P_M1A3_RT1); also elsewhere on the board
mA4: U9.C16 (L33N_A14_M1A4_RT1); also elsewhere on the board
mA5: U9.J11 (L40P_GCLK11_M1A5_RT1); also elsewhere on the board
mA6: U9.J12 (L40N_GCLK10_M1A6_RT1); also elsewhere on the board
mA7: U9.F15 (L35P_A11_M1A7_RT1); also elsewhere on the board
mA8: U9.F13 (L32P_A17_M1A8_RT1); also elsewhere on the board
mA9: U9.F14 (L32N_A16_M1A9_RT1); also elsewhere on the board
mA10: U9.C15 (L33P_A15_M1A10_RT1); also elsewhere on the board
mA11: U9.G11 (L30N_A20_M1A11_RT1); also elsewhere on the board
mA12: U9.D16 (L32N_A18_M1A12_RT1); also elsewhere on the board
mA13: U9.B15 (L29P_A23_M1A13_RT1); also elsewhere on the board
mA14: U9.B16 (L29N_A22_M1A14_RT1); also elsewhere on the board
mBA0: U9.G14 (L36P_A9_M1BA0_RT1); also elsewhere on the board
mBA1: U9.G16 (L36N_A8_M1BA1_RT1); also elsewhere on the board
mBA2: U9.E16 (L34N_A12_M1BA2_RT1); also elsewhere on the board
mCKE: U9.D14 (L31P_A19_M1CKE_RT1); also elsewhere on the board
mCLK: U9.G12 (L38P_A5_M1CLK_RT1); also elsewhere on the board
mD0: U9.M15 (L46P_FCS_B_M1DQ2_RB1); also elsewhere on the board
mD1: U9.K15 (L44P_A3_M1DQ6_RB1); also elsewhere on the board
mD2: U9.M16 (L46N_FOE_B_M1DQ3_RB1); also elsewhere on the board
mD3: U9.K16 (L44N_A2_M1DQ7_RB1); also elsewhere on the board
mD4: U9.L16 (L47N_LDC_M1DQ1_RB1); also elsewhere on the board
mD5: U9.J16 (L43N_GCLK4_M1DQ5_RB1); also elsewhere on the board
mD6: U9.L14 (L47P_FWE_B_M1DQ0_RB1); also elsewhere on the board
mD7: U9.J14 (L43P_GCLK5_M1DQ4_RB1); also elsewhere on the board
mD8: U9.P16 (L48N_M1DQ9_RB1); also elsewhere on the board
mD9: U9.T14 (L51P_M1DQ12_RB1); also elsewhere on the board
mD10: U9.P15 (L48P_HDC_M1DQ8_RB1); also elsewhere on the board
mD11: U9.T13 (L51N_M1DQ13_RB1); also elsewhere on the board
mD12: U9.R15 (L49P_M1DQ10_RB1); also elsewhere on the board
mD13: U9.T12 (L52N_M1DQ15_RB1); also elsewhere on the board
mD14: U9.R16 (L49N_M1DQ11_RB1); also elsewhere on the board
mD15: U9.R12 (L52P_M1DQ14_RB1); also elsewhere on the board
mLDM: U9.K11 (L42N_GCLK6_TRDY1_M1LDM_RB1); also elsewhere on the board
mLDQS: U9.N14 (L45P_A1_M1LDQS_RB1); also elsewhere on the board
mODT: U9.H14 (L39N_M1ODT_RT1); also elsewhere on the board
mRESET: U9.F12 (L30P_A21_M1RESET_RT1); also elsewhere on the board
mUDM: U9.K12 (L42P_GCLK7_M1UDM_RB1); also elsewhere on the board
mUDQS: U9.R14 (L50P_M1UDQS_RB1); also elsewhere on the board
mVREF: U9.E12 (L1N_A24_VREF_RT1), U9.L13 (L53N_VREF_RB1); also elsewhere on the board
macCKO: U9.C9 (L34P_GCLK19_TL0); also elsewhere on the board
macMCLK: U9.G1 (L40N_M3DQ7_LB3); also elsewhere on the board
macMDIO: U9.F2 (L41P_GCLK27_M3DQ4_LB3); also elsewhere on the board
macRXCLK: U9.H3 (L44N_GCLK20_M3A6_LT3); also elsewhere on the board
macRXCTL: U9.H1 (L39N_M3LDQSN_LB3); also elsewhere on the board
macRXD0: U9.H2 (L39P_M3LDQS_LB3); also elsewhere on the board
macRXD1: U9.J1 (L38N_M3DQ3_LB3); also elsewhere on the board
macRXD2: U9.J3 (L38P_M3DQ2_LB3); also elsewhere on the board
macRXD3: U9.K1 (L37N_M3DQ1_LB3); also elsewhere on the board
macTXCLK: U9.L1 (L36N_M3DQ9_LB3); also elsewhere on the board
macTXCTL: U9.K2 (L37P_M3DQ0_LB3); also elsewhere on the board
macTXD0: U9.N1 (L34N_M3UDQSN_LB3); also elsewhere on the board
macTXD1: U9.M2 (P35P_M3DQ10_LB3); also elsewhere on the board
macTXD2: U9.M1 (L35N_M3DQ11_LB3); also elsewhere on the board
macTXD3: U9.M3 (L1N_VREF_LB3); also elsewhere on the board
mnCAS: U9.K14 (L41N_GCLK8_M1CASN_RT1); also elsewhere on the board
mnCLK: U9.H11 (L38N_A4_M1CLKN_RT1); also elsewhere on the board
mnLDQS: U9.N16 (L45N_A0_M1LDQSN_RB1); also elsewhere on the board
mnRAS: U9.J13 (L41P_GCLK9_IRDY1_M1RASN_RT1); also elsewhere on the board
mnUDQS: U9.T15 (L50N_M1UDQSN_RB1); also elsewhere on the board
mnWE: U9.E15 (L34P_A13_M1WE_RT1); also elsewhere on the board
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

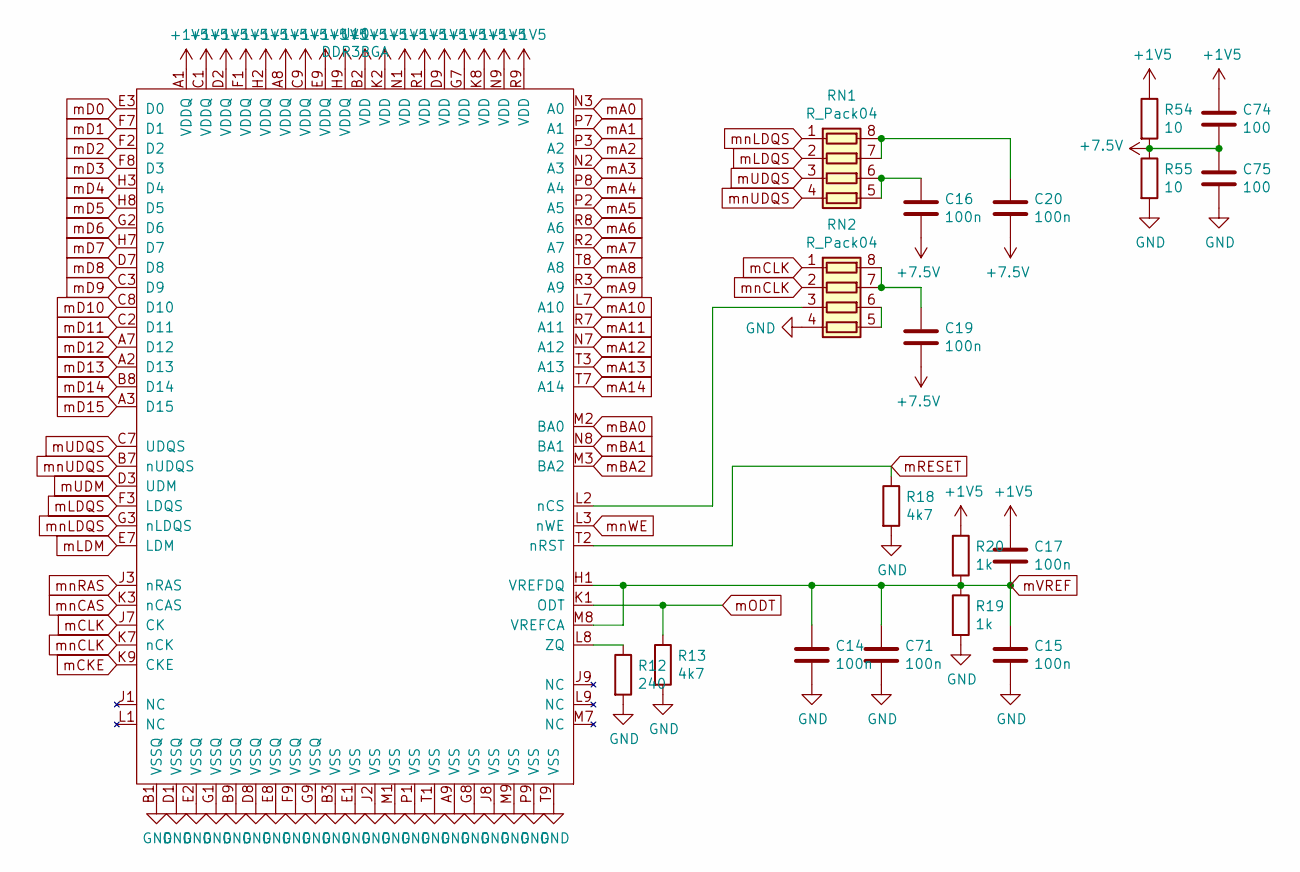
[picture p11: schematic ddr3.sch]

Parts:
C14, C15, C16, C17, C19, C20, C71: 100n; C_0805_2012Metric_Pad1.15x1.40mm_HandSolder
C74, C75: 100; C_0805_2012Metric_Pad1.15x1.40mm_HandSolder
R12: 240; R_0805_2012Metric_Pad1.15x1.40mm_HandSolder
R13, R18: 4k7; R_0805_2012Metric_Pad1.15x1.40mm_HandSolder
R19, R20: 1k; R_0805_2012Metric_Pad1.15x1.40mm_HandSolder
R54, R55: 10; R_0805_2012Metric_Pad1.15x1.40mm_HandSolder
RN1, RN2: R_Pack04; R_Array_Concave_4x0603
U10: DDR3BGA; ddr3bga

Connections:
+1V5: C17.1, C74.1, R20.1, R54.1, U10.A1 (VDDQ), U10.A8 (VDDQ), U10.B2 (VDD), U10.C1 (VDDQ), U10.C9 (VDDQ), U10.D2 (VDDQ), U10.D9 (VDD), U10.E9 (VDDQ), U10.F1 (VDDQ), U10.G7 (VDD), U10.H2 (VDDQ), U10.H9 (VDDQ), U10.K2 (VDD), U10.K8 (VDD), U10.N1 (VDD), U10.N9 (VDD), U10.R1 (VDD), U10.R9 (VDD); also elsewhere on the board
+7.5V: C16.2, C19.2, C20.2, C74.2, C75.1, R54.2, R55.1
GND: C14.2, C15.2, C71.2, C75.2, R12.2, R13.2, R18.2, R19.2, R55.2, RN2.4 (R4.1), U10.A9 (VSS), U10.B1 (VSSQ), U10.B3 (VSS), U10.B9 (VSSQ), U10.D1 (VSSQ), U10.D8 (VSSQ), U10.E1 (VSS), U10.E2 (VSSQ), U10.E8 (VSSQ), U10.F9 (VSSQ), U10.G1 (VSSQ), U10.G8 (VSS), U10.G9 (VSSQ), U10.J2 (VSS), U10.J8 (VSS), U10.M1 (VSS), U10.M9 (VSS), U10.P1 (VSS), U10.P9 (VSS), U10.T1 (VSS), U10.T9 (VSS); also elsewhere on the board
unnamed: C16.1, RN1.5 (R4.2), RN1.6 (R3.2)
unnamed: C19.1, RN2.7 (R2.2), RN2.8 (R1.2)
unnamed: C20.1, RN1.7 (R2.2), RN1.8 (R1.2)
unnamed: R12.1, U10.L8 (ZQ)
unnamed: RN2.3 (R3.1), U10.L2 (nCS)
unnamed: RN2.5 (R4.2), RN2.6 (R3.2)
mA0: U10.N3 (A0); also elsewhere on the board
mA1: U10.P7 (A1); also elsewhere on the board
mA2: U10.P3 (A2); also elsewhere on the board
mA3: U10.N2 (A3); also elsewhere on the board
mA4: U10.P8 (A4); also elsewhere on the board
mA5: U10.P2 (A5); also elsewhere on the board
mA6: U10.R8 (A6); also elsewhere on the board
mA7: U10.R2 (A7); also elsewhere on the board
mA8: U10.T8 (A8); also elsewhere on the board
mA9: U10.R3 (A9); also elsewhere on the board
mA10: U10.L7 (A10); also elsewhere on the board
mA11: U10.R7 (A11); also elsewhere on the board
mA12: U10.N7 (A12); also elsewhere on the board
mA13: U10.T3 (A13); also elsewhere on the board
mA14: U10.T7 (A14); also elsewhere on the board
mBA0: U10.M2 (BA0); also elsewhere on the board
mBA1: U10.N8 (BA1); also elsewhere on the board
mBA2: U10.M3 (BA2); also elsewhere on the board
mCKE: U10.K9 (CKE); also elsewhere on the board
mCLK: RN2.1 (R1.1), U10.J7 (CK); also elsewhere on the board
mD0: U10.E3 (D0); also elsewhere on the board
mD1: U10.F7 (D1); also elsewhere on the board
mD2: U10.F2 (D2); also elsewhere on the board
mD3: U10.F8 (D3); also elsewhere on the board
mD4: U10.H3 (D4); also elsewhere on the board
mD5: U10.H8 (D5); also elsewhere on the board
mD6: U10.G2 (D6); also elsewhere on the board
mD7: U10.H7 (D7); also elsewhere on the board
mD8: U10.D7 (D8); also elsewhere on the board
mD9: U10.C3 (D9); also elsewhere on the board
mD10: U10.C8 (D10); also elsewhere on the board
mD11: U10.C2 (D11); also elsewhere on the board
mD12: U10.A7 (D12); also elsewhere on the board
mD13: U10.A2 (D13); also elsewhere on the board
mD14: U10.B8 (D14); also elsewhere on the board
mD15: U10.A3 (D15); also elsewhere on the board
mLDM: U10.E7 (LDM); also elsewhere on the board
mLDQS: RN1.2 (R2.1), U10.F3 (LDQS); also elsewhere on the board
mODT: R13.1, U10.K1 (ODT); also elsewhere on the board
mRESET: R18.1, U10.T2 (nRST); also elsewhere on the board
mUDM: U10.D3 (UDM); also elsewhere on the board
mUDQS: RN1.3 (R3.1), U10.C7 (UDQS); also elsewhere on the board
mVREF: C14.1, C15.1, C17.2, C71.1, R19.1, R20.2, U10.H1 (VREFDQ), U10.M8 (VREFCA); also elsewhere on the board
mnCAS: U10.K3 (nCAS); also elsewhere on the board
mnCLK: RN2.2 (R2.1), U10.K7 (nCK); also elsewhere on the board
mnLDQS: RN1.1 (R1.1), U10.G3 (nLDQS); also elsewhere on the board
mnRAS: U10.J3 (nRAS); also elsewhere on the board
mnUDQS: RN1.4 (R4.1), U10.B7 (nUDQS); also elsewhere on the board
mnWE: U10.L3 (nWE); also elsewhere on the board

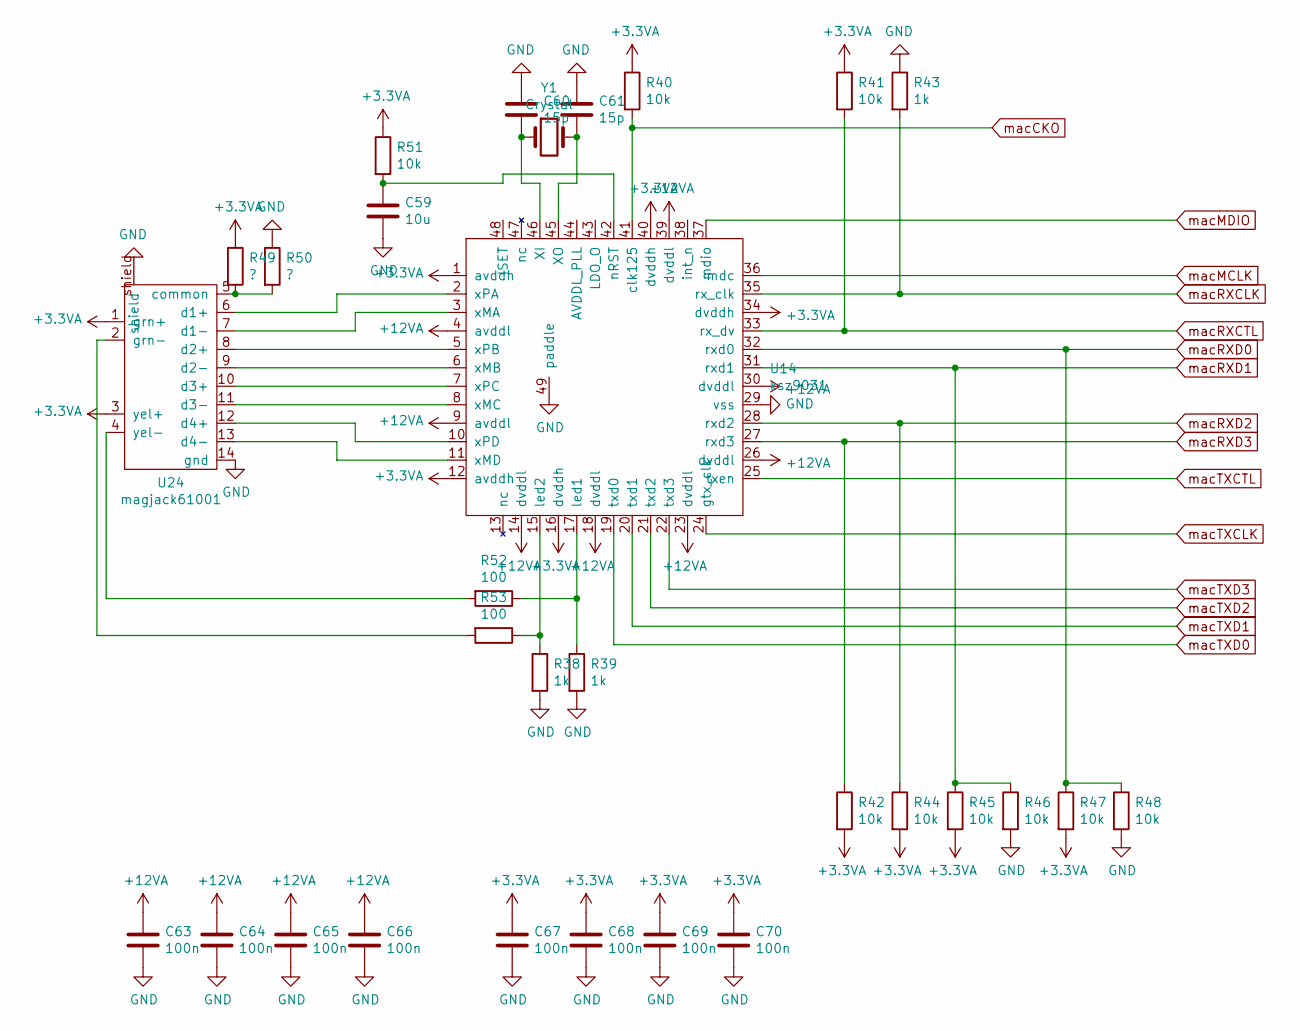
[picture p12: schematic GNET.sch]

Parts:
C59: 10u; C_0805_2012Metric_Pad1.15x1.40mm_HandSolder
C60, C61: 15p; C_0805_2012Metric_Pad1.15x1.40mm_HandSolder
C63, C64, C65, C66, C67, C68, C69, C70: 100n; C_0805_2012Metric_Pad1.15x1.40mm_HandSolder
R38, R39, R43: 1k; R_0805_2012Metric_Pad1.15x1.40mm_HandSolder
R40, R41, R42, R44, R45, R46, R47, R48, R51: 10k; R_0805_2012Metric_Pad1.15x1.40mm_HandSolder
R49, R50: ?; R_0805_2012Metric_Pad1.15x1.40mm_HandSolder
R52, R53: 100; R_0805_2012Metric_Pad1.15x1.40mm_HandSolder
U14: ksz9031; qfn49_0.5_7x7
U24: magjack61001
Y1: Crystal; xtal

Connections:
+3.3VA: C67.1, C68.1, C69.1, C70.1, R40.1, R41.1, R42.2, R44.2, R45.2, R47.2, R49.1, R51.1, U14.1 (avddh), U14.12 (avddh), U14.16 (dvddh), U14.34 (dvddh), U14.40 (dvddh), U24.1 (grn+), U24.3 (yel+); also elsewhere on the board
+12VA: C63.1, C64.1, C65.1, C66.1, U14.4 (avddl), U14.9 (avddl), U14.14 (dvddl), U14.18 (dvddl), U14.23 (dvddl), U14.26 (dvddl), U14.30 (dvddl), U14.39 (dvddl); also elsewhere on the board
GND: C59.2, C60.1, C61.1, C63.2, C64.2, C65.2, C66.2, C67.2, C68.2, C69.2, C70.2, R38.2, R39.2, R43.1, R46.2, R48.2, R50.1, U14.29 (vss), U14.49 (paddle), U24.14 (gnd), U24.shield; also elsewhere on the board
unnamed: C59.1, R51.2, U14.42 (nRST)
unnamed: C60.2, U14.46 (XI), Y1.1
unnamed: C61.2, U14.45 (XO), Y1.2
unnamed: R38.1, R53.1, U14.15 (led2)
unnamed: R39.1, R52.1, U14.17 (led1)
unnamed: R49.2, R50.2, U24.5 (common)
unnamed: R52.2, U24.4 (yel-)
unnamed: R53.2, U24.2 (grn-)
unnamed: U14.2 (xPA), U24.6 (d1+)
unnamed: U14.3 (xMA), U24.7 (d1-)
unnamed: U14.5 (xPB), U24.8 (d2+)
unnamed: U14.6 (xMB), U24.9 (d2-)
unnamed: U14.7 (xPC), U24.10 (d3+)
unnamed: U14.8 (xMC), U24.11 (d3-)
unnamed: U14.10 (xPD), U24.12 (d4+)
unnamed: U14.11 (xMD), U24.13 (d4-)
macCKO: R40.2, U14.41 (clk125); also elsewhere on the board
macMCLK: U14.36 (mdc); also elsewhere on the board
macMDIO: U14.37 (mdio); also elsewhere on the board
macRXCLK: R43.2, U14.35 (rx_clk); also elsewhere on the board
macRXCTL: R41.2, U14.33 (rx_dv); also elsewhere on the board
macRXD0: R47.1, R48.1, U14.32 (rxd0); also elsewhere on the board
macRXD1: R45.1, R46.1, U14.31 (rxd1); also elsewhere on the board
macRXD2: R44.1, U14.28 (rxd2); also elsewhere on the board
macRXD3: R42.1, U14.27 (rxd3); also elsewhere on the board
macTXCLK: U14.24 (gtx_clk); also elsewhere on the board
macTXCTL: U14.25 (txen); also elsewhere on the board
macTXD0: U14.19 (txd0); also elsewhere on the board
macTXD1: U14.20 (txd1); also elsewhere on the board
macTXD2: U14.21 (txd2); also elsewhere on the board
macTXD3: U14.22 (txd3); also elsewhere on the board

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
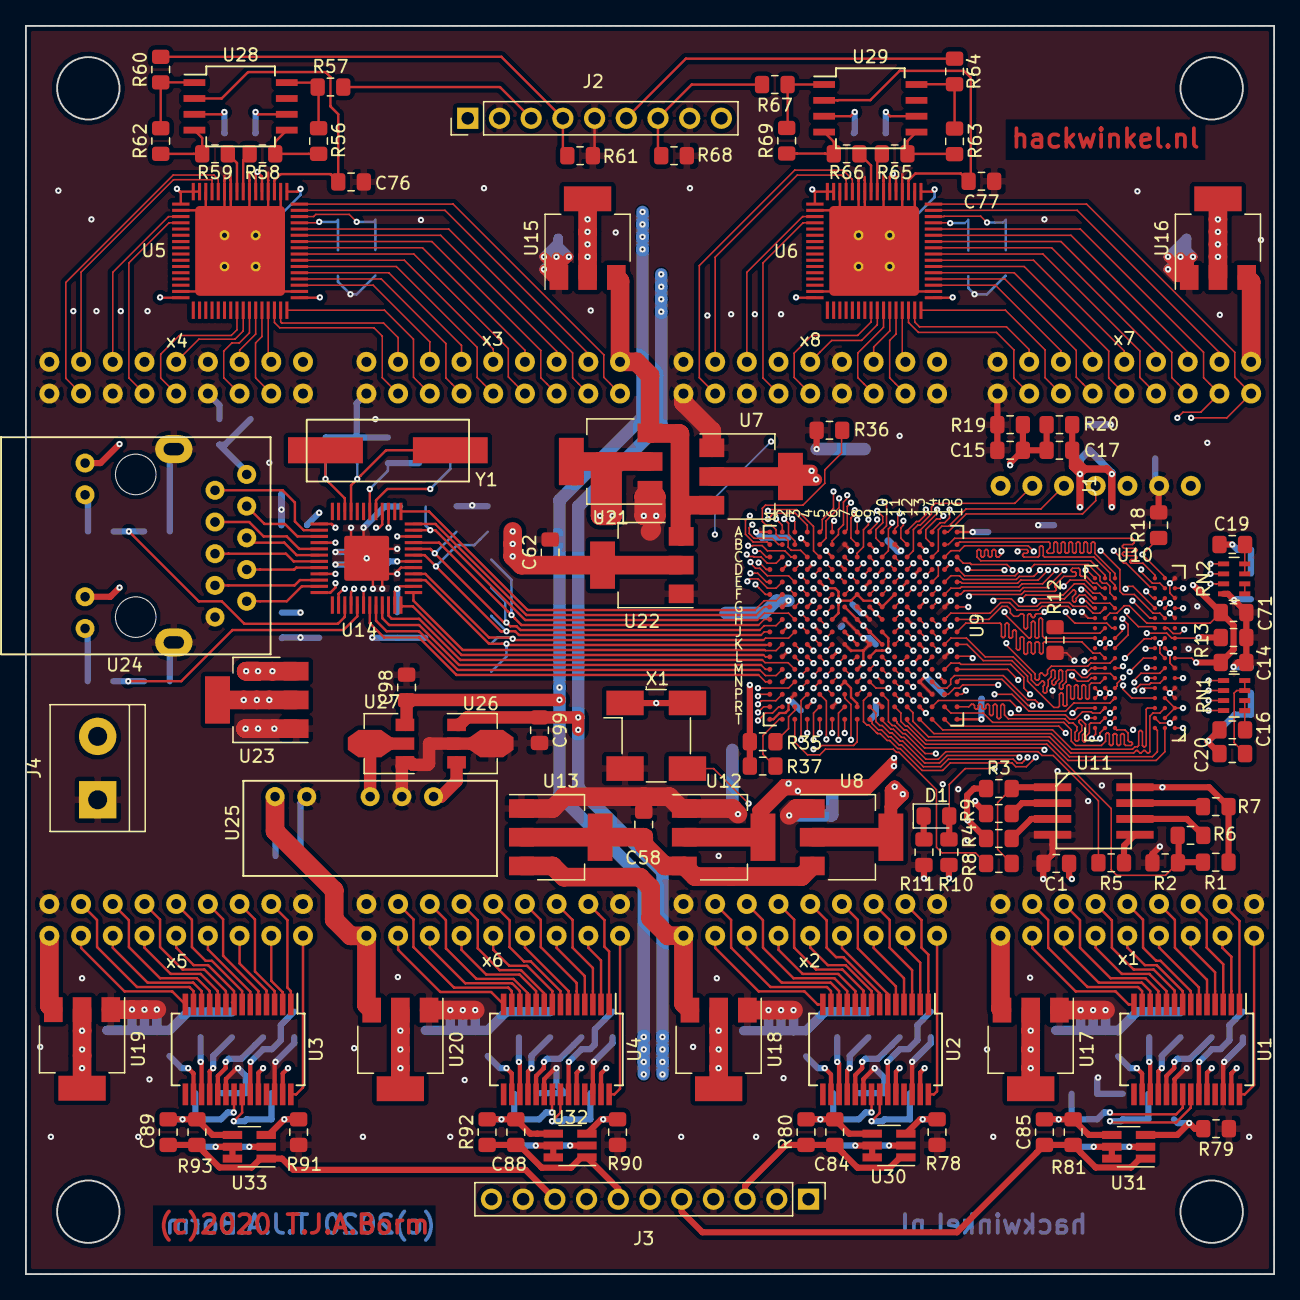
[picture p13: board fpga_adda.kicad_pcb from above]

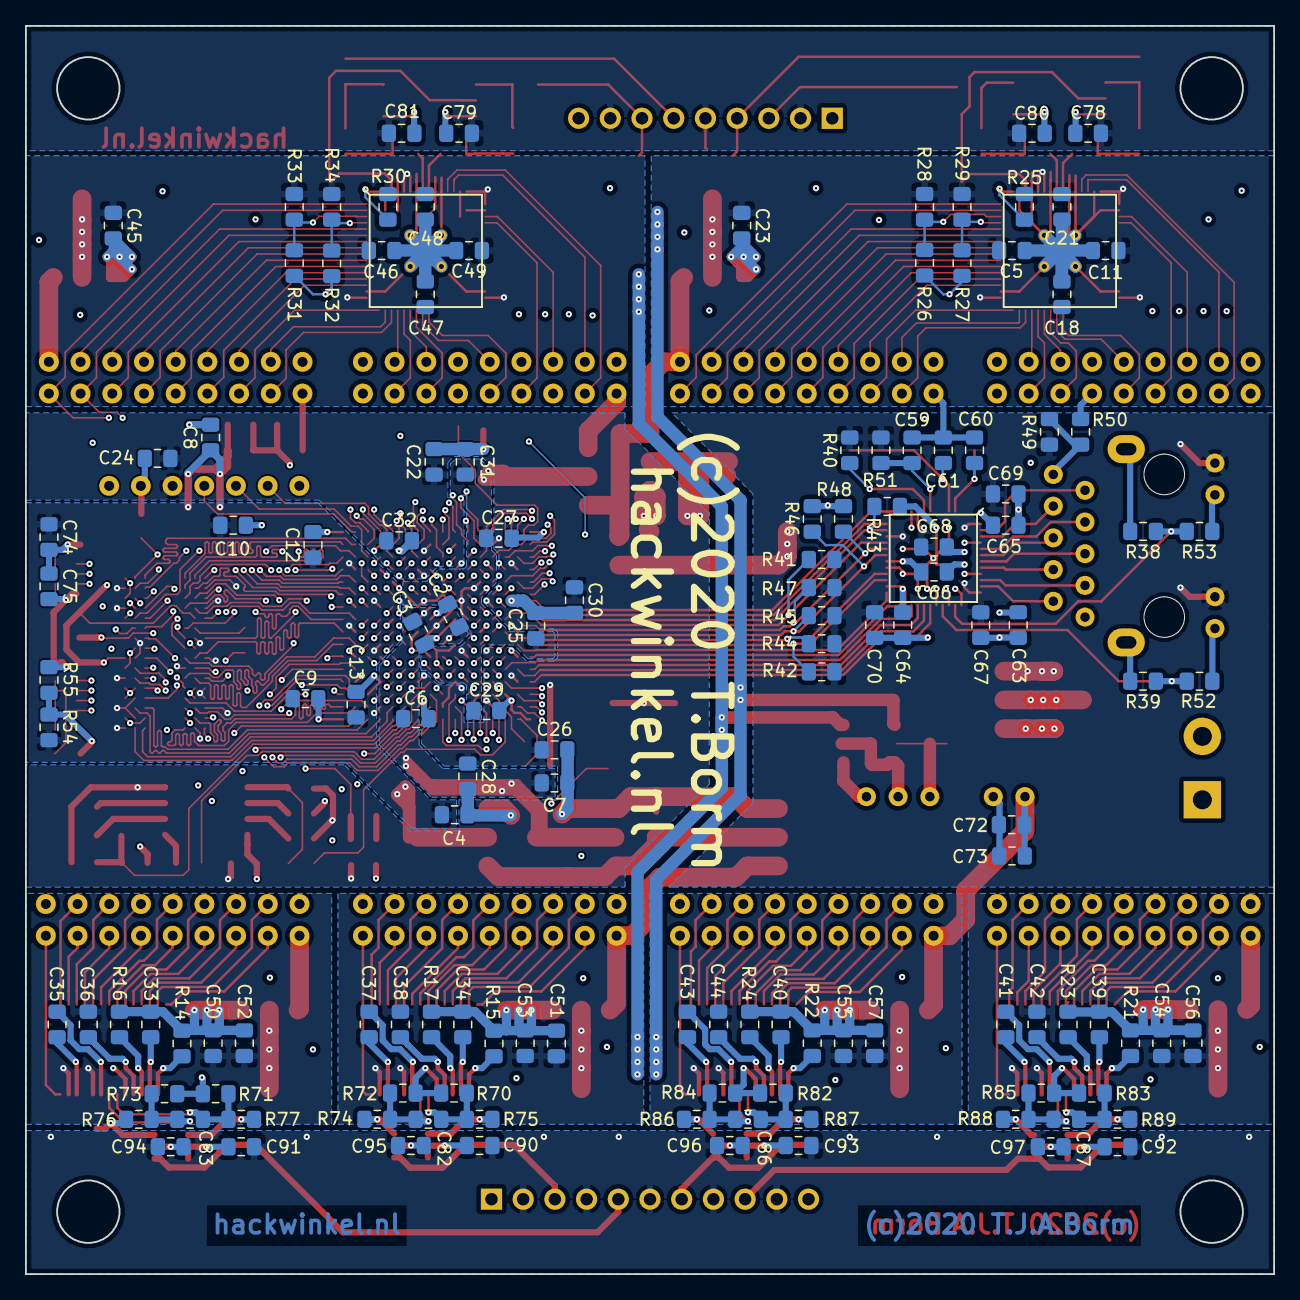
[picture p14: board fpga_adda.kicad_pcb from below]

Board: 4 copper layers, 100.0 x 100.0 mm, 242 parts (133 on the bottom side), 300 nets.

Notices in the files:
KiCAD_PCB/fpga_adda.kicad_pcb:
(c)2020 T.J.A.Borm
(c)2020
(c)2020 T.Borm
